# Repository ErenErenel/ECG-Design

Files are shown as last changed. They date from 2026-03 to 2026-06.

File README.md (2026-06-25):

# ECG Instrumentation & Heart Rate Variability Analysis

An analog ECG front-end (instrumentation amplifier + filtering) built around the
**OP484** quad op-amp, together with a Python analysis of the acquired signal for
beat-by-beat heart rate and heart rate variability (HRV).

Developed for the **EE 495 ECG Lab** at Northwestern University.

## Analog Front-End

A Lead-I ECG is acquired with RA and LA as the differential inputs and RL as the
right-leg reference ground. The signal chain runs on a single OP484 (four op-amps,
±5 V supply):

- **Instrumentation amplifier (3 op-amps)** — total gain ≈ 25
  - First stage (differential): G₁ = (2R₂ + R₁)/R₁ = 5, with R₂ = 20 kΩ, R₁ = 10 kΩ
  - Second stage (difference amp): G₂ = R₆/R₄ = 5, with R₆ = 100 kΩ, R₄ = 20 kΩ
- **Gain + filtering stage (4th op-amp)** — additional gain and approximate
  1–100 Hz band-limiting (high-pass + low-pass) to suppress baseline drift and
  high-frequency interference.

Bench verification with a 10 mV differential sine drove an output near 0.25 V,
confirming the ×25 instrumentation-amp gain across the 1–1000 Hz range.

## Heart Rate & HRV Analysis

A ~1-minute Lead-I recording was digitized at **fₛ = 1000 Hz** and analyzed in Python:

- **R-peak detection** — threshold-based (750 mV) with a 0.25 s refractory period and
  recovery of missed beats from abnormally long RR intervals. **72 R-peaks** detected.
- **Beat-by-beat heart rate** — computed from RR intervals (HRᵢ = 60 / RRᵢ),
  starting around 74.6 bpm.
- **HRV spectral analysis** — the mean HR is removed and an FFT-based power spectrum
  of the HR signal shows most variability at low frequencies (≤ 2 Hz, with a bump near
  ~0.18 Hz) associated with autonomic / respiratory modulation.

## Repository Structure

```
ECG-Design/
├── ECG PCB Files/          KiCad schematic, layout, and project for the ECG board
│   ├── ECG.kicad_sch
│   ├── ECG.kicad_pcb
│   └── ECG.kicad_pro
├── EE495 ECG Lab.pdf       Lab report: instrumentation amp design + ECG acquisition
└── Heart Rate Variability Analysis.pdf
                            HR and HRV analysis of the recorded ECG
```

Open `ECG PCB Files/ECG.kicad_pro` in **KiCad 7+** to view the schematic and board.

## License

Released under the [MIT License](LICENSE).

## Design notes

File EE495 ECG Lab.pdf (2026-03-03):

# EE495 ECG Lab Project

## Part 1: Instrumentation Amplifier

The instrumentation amplifier (Figure 1) was implemented using three OP484 op-amps powered by ±5 V.

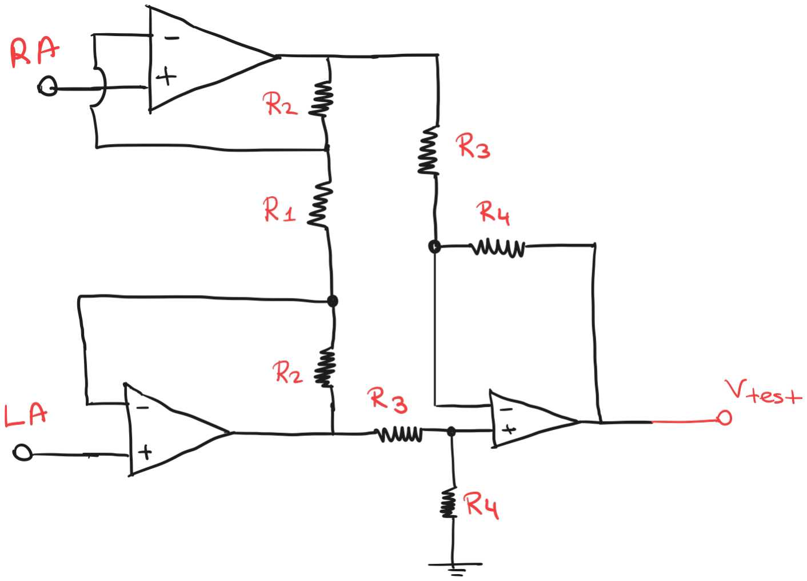
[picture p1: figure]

Figure 1: Instrumentation amplifier schematic

First stage (differential) gain G! = 2R" + R!
R!

with R" = 20 kΩ, R! = 10 kΩ:
G! = 2(20k) + 10k

10k = 50k 10k = 5

Second stage (difference amplifier) gain G" = R#
R$

with R# = 100 kΩ, R$ = 20 kΩ:
G" = 100k
20k = 5
Total instrumentation amplifier gain GINA = G!G" = 5 × 5 = 25

Bench verification: The amplifier was driven using a 10 mV differential sine wave generated by the Analog Discovery through a resistor attenuator. The measured output amplitude at Vtest was approximately 0.25 V, confirming a gain near 25 across the 1–1000 Hz test range.

ECG acquisition: A Lead-I ECG was acquired with RA and LA as the differential inputs and RL as the reference (right-leg ground). The resulting waveform (Plot 1) shows ECG morphology with noticeable high-frequency interference and baseline drift typical of unfiltered acquisition.

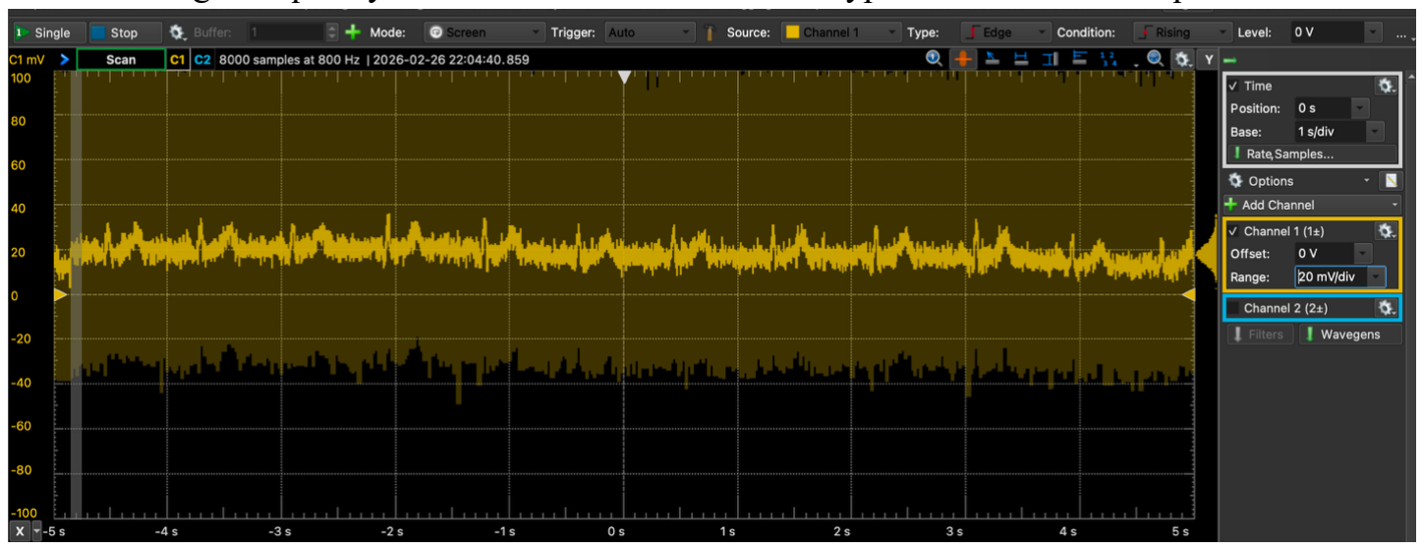
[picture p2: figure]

Plot 1: Lead-I ECG after instrumentation amplifier (G ≈ 25)

## Part 2: Additional Amplification + Filtering

The fourth OP484 op-amp was used to add additional gain and implement approximate 1–100 Hz band-limiting (Figure 2).

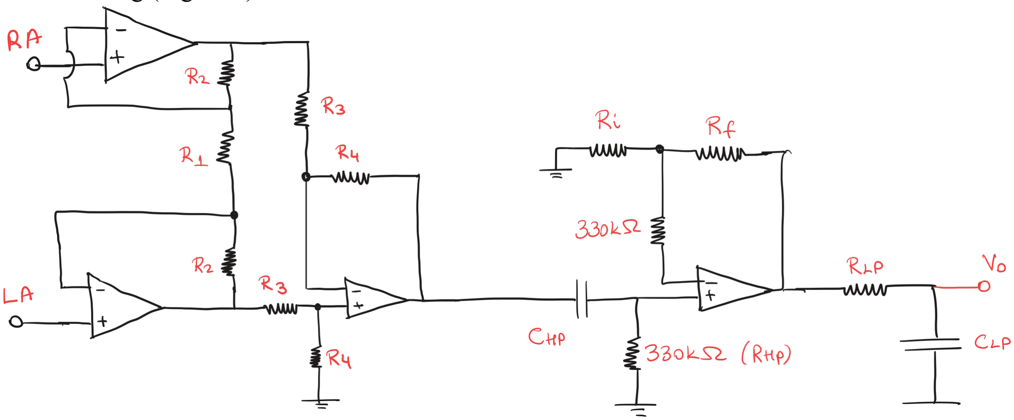
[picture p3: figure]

Figure 2: Full ECG amplifier circuit (INA + filter/gain stage)

High-pass filter
f%& = 1 2πR%&C%&

with R%& = 330 kΩ, C%& = 0.47 μF:
f%& = | 1
2π(330k)(0.47μ) ≈ 1.03 Hz

This attenuates electrode DC offset and low-frequency baseline drift.

Second-stage non-inverting gain

Gstage2 = 1 +

R'
R⁽

with R' = 330 kΩ, R⁽ = 33 kΩ:

Gstage2 = 1 +

330k
33k = 11

Low-pass filter (noise reduction) f)& = 1
2πR)&C)&

with R)& = 33 kΩ, C)& = 0.047 μF:
f)& = | 1
2π(33k)(0.047μ) ≈ 103 Hz

This significantly reduces high-frequency noise while preserving QRS morphology.

Overall gain
Gtotal = GINA ⋅ Gstage2 = 25 × 11 = 275

## ECG acquisition

Lead-I ECG was recorded again using the complete amplifier. Compared to Part 1, the final output (Plot 2) shows substantially reduced high-frequency interference and improved readability of ECG features.

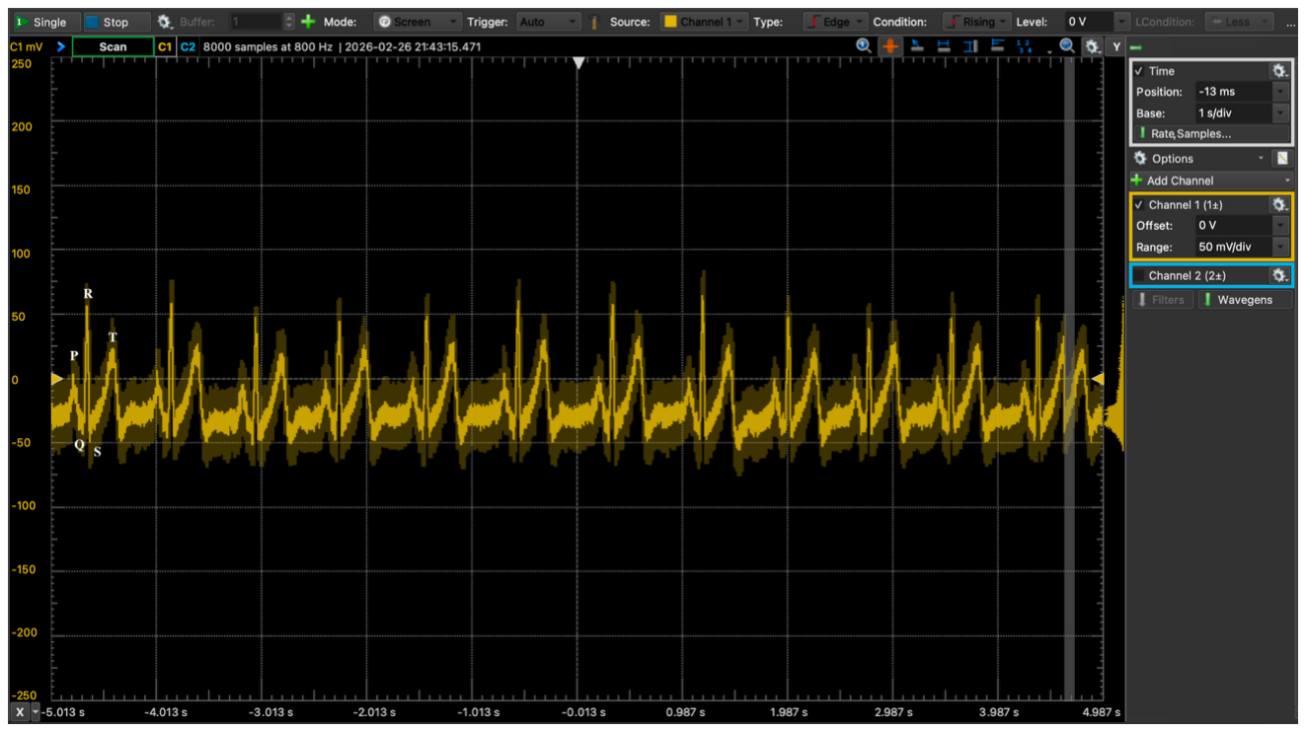
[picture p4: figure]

Plot 2: Lead-I ECG after full amplifier (G ≈ 275, ~1–100 Hz)

## Digitization and Digital Post-Processing (1-minute recording)

A continuous 1-minute Lead-I ECG recording was stored using the Analog Discovery in 16-bit signed binary format at a 1024 Hz sampling rate for analysis in Python. For visualization, a digital 60 Hz notch filter was applied to further suppress power-line interference.

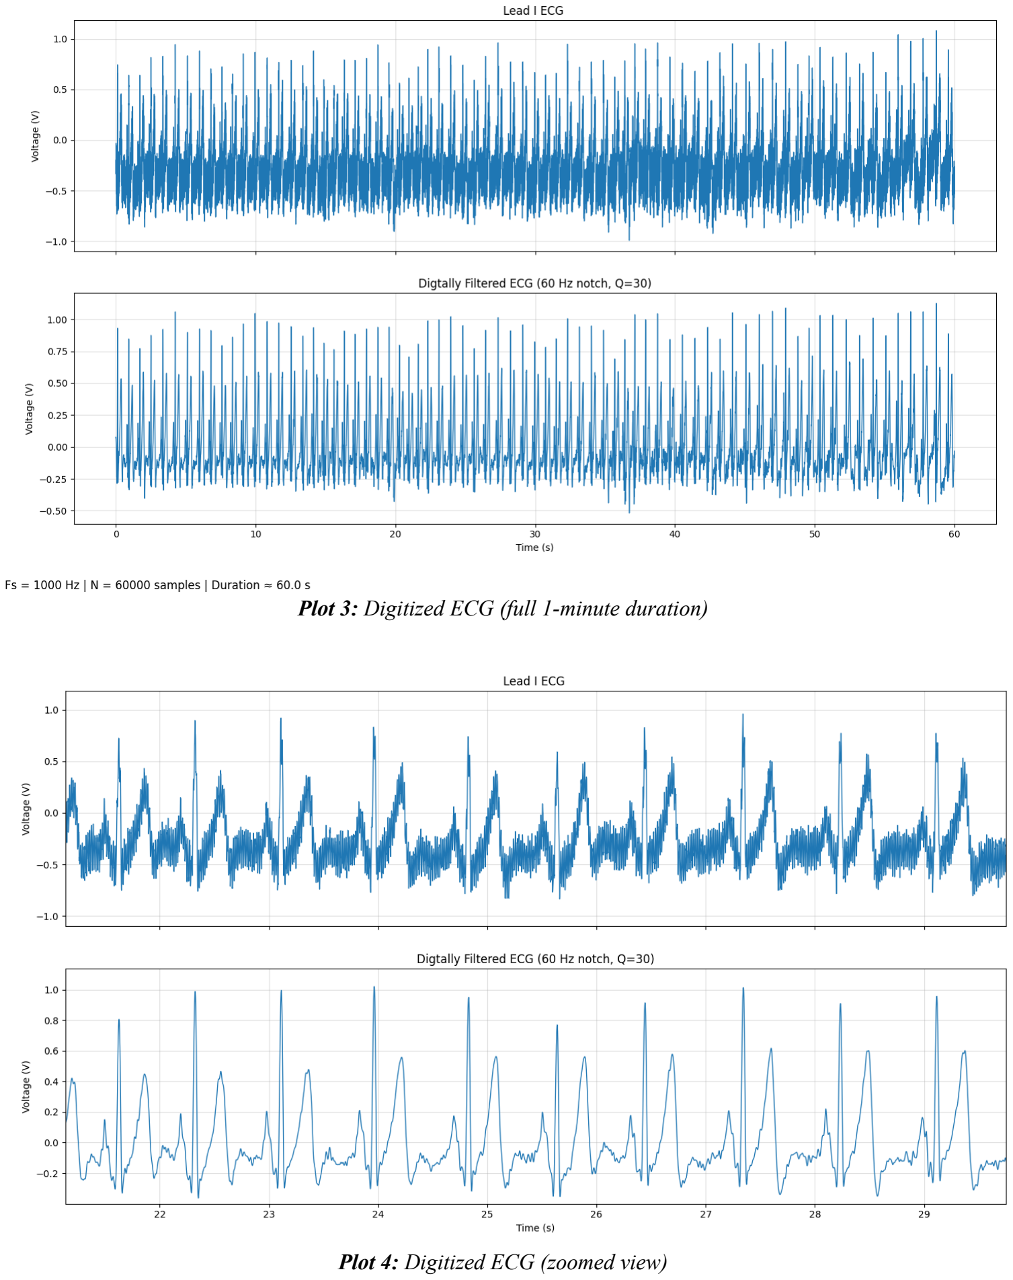
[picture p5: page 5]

Plot 3: Digitized ECG (full 1-minute duration)

Plot 4: Digitized ECG (zoomed view)

In the zoomed view (Plot 4), removing 60 Hz interference improves visibility of lower-amplitude features; in particular, a small post–T-wave deflection that could indicate a U wave is more clearly resolved rather than being masked by high-frequency noise.

Appendix:
import numpy as np
import matplotlib.pyplot as plt
from scipy.signal import filtfilt, iirnotch

# User settings

fs = 1000.0
path = "/Users/erenerenel/Desktop/EE495/EE495 Code/default.csv"

NOTCH_HZ = 60.0
NOTCH_Q = 30.0

# Load CSV

data = np.genfromtxt(path, delimiter=",", comments="#", invalid_raise=False) data = np.atleast_2d(data)
data = data[~np.all(np.isnan(data), axis=1)]

print("Loaded shape:", data.shape)
if data.shape[0] < 1000:
raise ValueError("CSV loaded too few rows")

col0 = data[:, 0]
is_time_like = np.all(np.diff(col0[:200]) > 0) and (np.nanmedian(np.diff(col0[:200])) < 0.05)

if data.shape[1] >= 2 and is_time_like:
t = col0
c1_volts = data[:, 1]
else:
c1_volts = data[:, 0]
t = np.arange(c1_volts.size) / fs

mask = ~np.isnan(c1_volts)
c1_volts = c1_volts[mask]
t = t[mask]

print("Samples:", c1_volts.size, "Duration(s):", (t[-1] - t[0]) if t.size else 0)

# Filtering

bN, aN = iirnotch(NOTCH_HZ, Q=NOTCH_Q, fs=fs)
ecg_filt = filtfilt(bN, aN, c1_volts)

# Plot

raw_mv = c1_volts / 1000
filt_mv = ecg_filt / 1000

fig, ax = plt.subplots(2, 1, sharex=True, figsize=(10, 6))

ax[0].plot(t, raw_mv, linewidth=1.0) ax[0].set_title("Lead I ECG ")
ax[0].set_ylabel("Voltage (V)") ax[0].grid(True, alpha=0.4)

ax[1].plot(t, filt_mv, linewidth=1.0)
ax[1].set_title(
f"Digtally Filtered ECG ({NOTCH_HZ:g} Hz notch, Q={NOTCH_Q:g})" )
ax[1].set_xlabel("Time (s)")
ax[1].set_ylabel("Voltage (V)")
ax[1].grid(True, alpha=0.4)

duration_s = t[-1] - t[0]
fig.text(
0.01, 0.01,
f"Fs = {fs:g} Hz | N = {len(t)} samples | Duration ≈ {duration_s:.1f} s",
fontsize=12
)

fig.tight_layout(rect=[0, 0.02, 1, 1]) plt.show()

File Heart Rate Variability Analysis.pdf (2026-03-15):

## Beat-by-Beat Heart Rate and Heart Rate Variability Analysis

## Introduction

An ECG signal recorded using the ECG instrumentation amplifier built during the laboratory exercise was analyzed to compute beat-by-beat heart rate (HR) and heart rate variability (HRV). The ECG was recorded in a Lead-I configuration with right-leg grounding for approximately one minute and digitized at a sampling rate of:
fs = 1000 Hz

All analysis was implemented in Python.

## 1. Beat-by-Beat Heart Rate Measurement

R-Peak Detection
R-peaks were detected from the ECG using a threshold-based algorithm:
1. A voltage threshold of 750 mV was used to identify candidate QRS complexes.
2. The local maximum within each threshold crossing was selected as the R-peak.
3. A refractory period of 0.25 s prevented multiple detections within the same QRS complex.
4. Missed beats were recovered by identifying abnormally large RR intervals and searching for the largest peak within that interval (as some of the R-peaks were below the set 750 mV).
A total of 72 R-peaks were detected in the one-minute ECG recording.

ECG with Detected Peaks

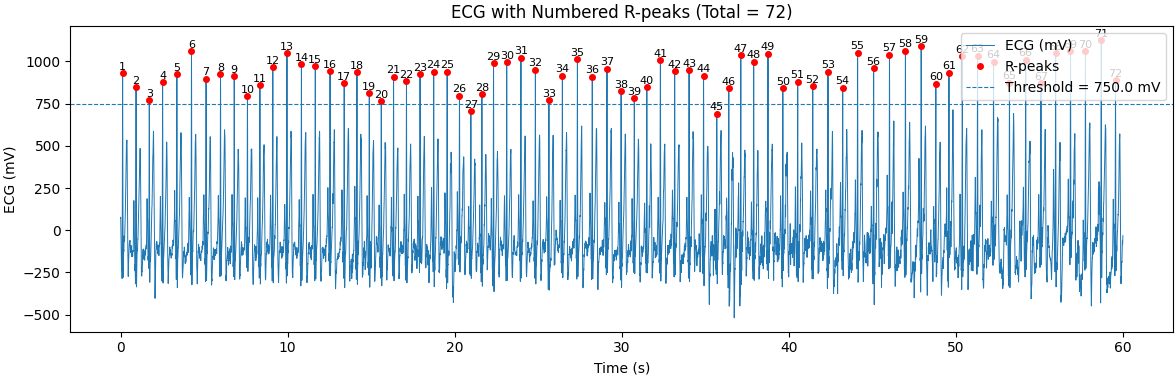
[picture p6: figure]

Figure 1: ECG recording used in the analysis with detected R-peaks labeled.

To improve visualization, the ECG was also segmented into groups of 24 beats.

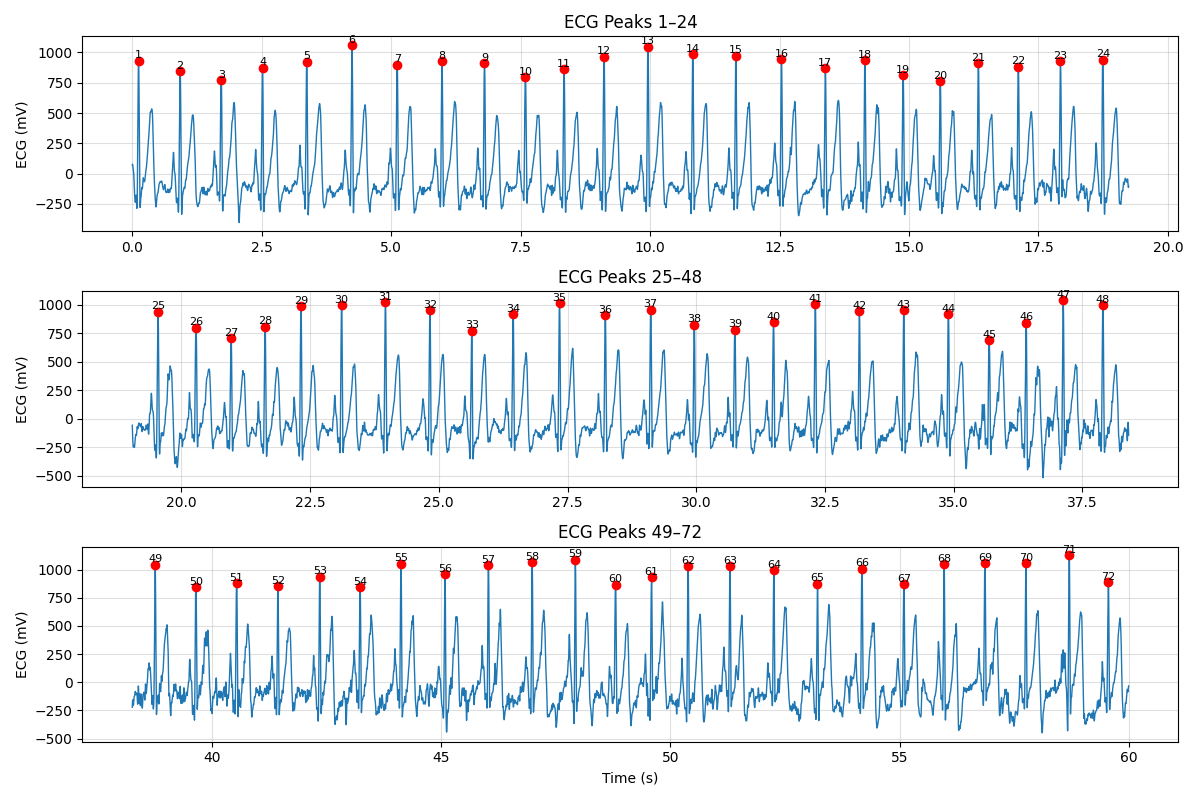
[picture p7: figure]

Figure 2: Segmented ECG plots showing detected peaks.

Beat-by-Beat Heart Rate
Heart rate was calculated from the RR intervals between consecutive R-peaks: RRi = ti − ti−1

HRi =

60
RRi

where RRi

is the interval between beats in seconds and HRi is the instantaneous heart rate in beats per minute (bpm).
The resulting values provide a beat-by-beat estimate of heart rate over the one-minute recording (Values in Appendix.A)

## 2. Heart Rate Variability

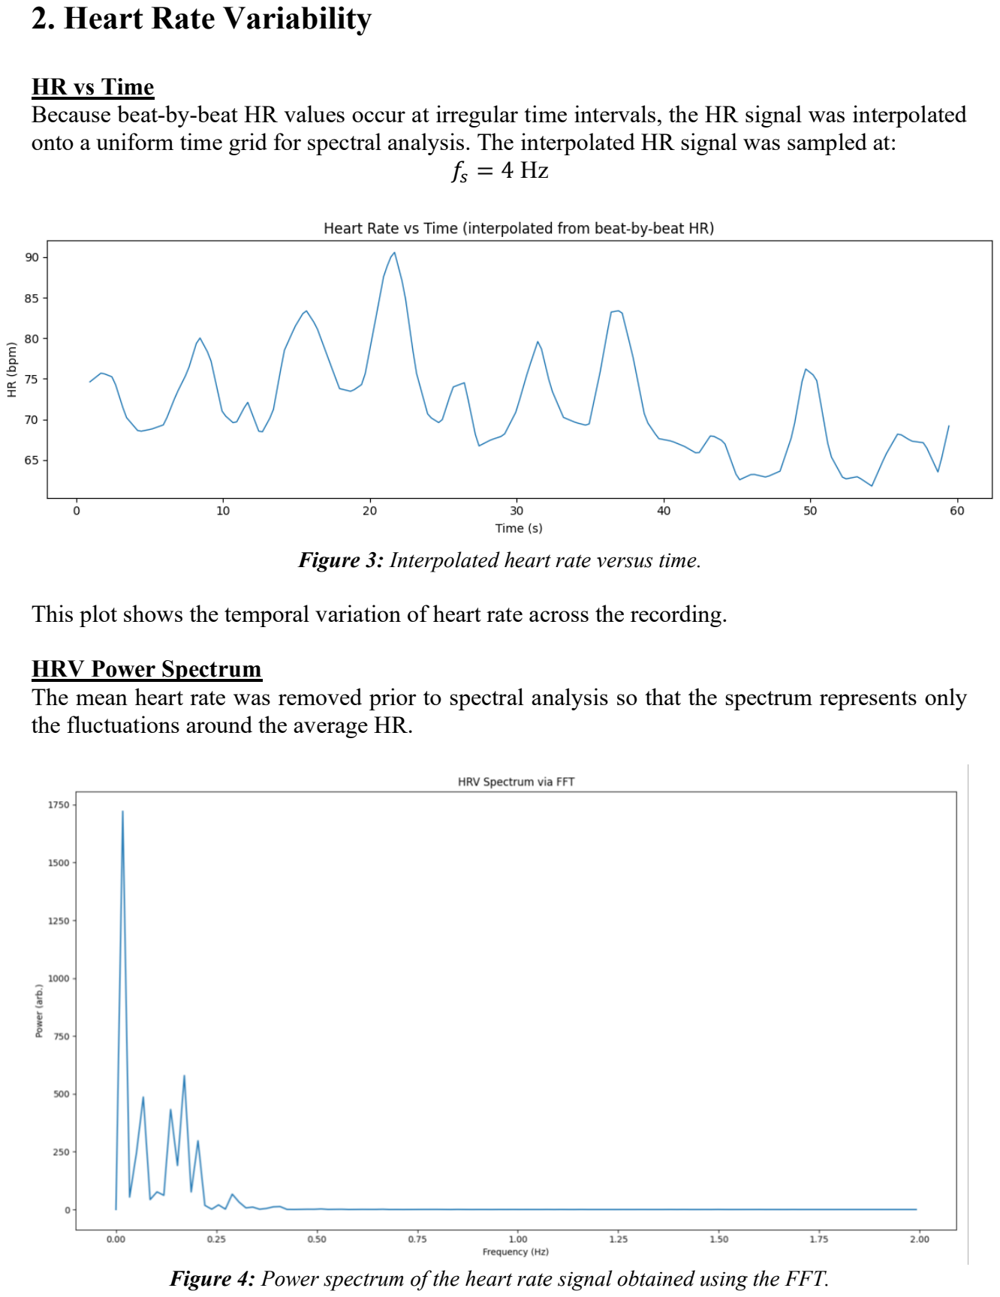
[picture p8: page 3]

HR vs Time
Because beat-by-beat HR values occur at irregular time intervals, the HR signal was interpolated onto a uniform time grid for spectral analysis. The interpolated HR signal was sampled at:
fs = 4 Hz

Figure 3: Interpolated heart rate versus time.

This plot shows the temporal variation of heart rate across the recording.

HRV Power Spectrum
The mean heart rate was removed prior to spectral analysis so that the spectrum represents only the fluctuations around the average HR.

Figure 4: Power spectrum of the heart rate signal obtained using the FFT.

The HRV spectrum shows that most variability occurs at low frequencies (≤ 2 Hz , especially the bump at ~ 0.18 Hz). These slow fluctuations are associated with the autonomic regulation of heart rate and indicative of the respiratory rate. Higher frequency components contain comparatively less power.

# Conclusion

Beat-by-beat heart rate and heart rate variability were successfully computed from a one-minute ECG recording. R-peaks were detected using a threshold-based method with refractory filtering and missed-beat recovery.
Heart rate was calculated from RR intervals and interpolated to form a uniformly sampled HR signal.
Spectral analysis of this signal revealed that HR variability is primarily concentrated at frequencies around 0.15 – 0.20 Hz.

*Code used in the report can be found in Appendix.B.

## Appendix

Appendix.A
Beat-by-beat HR list (bpm):
001: t = 0.925 s HR = 74.63 bpm 002: t = 1.717 s HR = 75.76 bpm 003: t = 2.515 s HR = 75.19 bpm 004: t = 3.368 s HR = 70.34 bpm 005: t = 4.244 s HR = 68.49 bpm 006: t = 5.116 s HR = 68.81 bpm 007: t = 5.981 s HR = 69.36 bpm 008: t = 6.802 s HR = 73.08 bpm 009: t = 7.592 s HR = 75.95 bpm 010: t = 8.339 s HR = 80.32 bpm 011: t = 9.111 s HR = 77.72 bpm 012: t = 9.959 s HR = 70.75 bpm 013: t = 10.824 s HR = 69.36 bpm 014: t = 11.655 s HR = 72.20 bpm 015: t = 12.537 s HR = 68.03 bpm 016: t = 13.384 s HR = 70.84 bpm 017: t = 14.149 s HR = 78.43 bpm 018: t = 14.886 s HR = 81.41 bpm 019: t = 15.604 s HR = 83.57 bpm 020: t = 16.340 s HR = 81.52 bpm 021: t = 17.112 s HR = 77.72 bpm 022: t = 17.925 s HR = 73.80 bpm 023: t = 18.742 s HR = 73.44 bpm 024: t = 19.548 s HR = 74.44 bpm 025: t = 20.285 s HR = 81.41 bpm 026: t = 20.967 s HR = 87.98 bpm 027: t = 21.627 s HR = 90.91 bpm 028: t = 22.324 s HR = 86.08 bpm 029: t = 23.113 s HR = 76.05 bpm 030: t = 23.965 s HR = 70.42 bpm 031: t = 24.829 s HR = 69.44 bpm 032: t = 25.640 s HR = 73.98 bpm 033: t = 26.445 s HR = 74.53 bpm 034: t = 27.345 s HR = 66.67 bpm

035: t = 28.234 s HR = 67.49 bpm 036: t = 29.116 s HR = 68.03 bpm 037: t = 29.961 s HR = 71.01 bpm 038: t = 30.751 s HR = 75.95 bpm 039: t = 31.501 s HR = 80.00 bpm 040: t = 32.313 s HR = 73.89 bpm 041: t = 33.167 s HR = 70.26 bpm 042: t = 34.029 s HR = 69.61 bpm 043: t = 34.896 s HR = 69.20 bpm 044: t = 35.686 s HR = 75.95 bpm 045: t = 36.407 s HR = 83.22 bpm 046: t = 37.126 s HR = 83.45 bpm 047: t = 37.897 s HR = 77.82 bpm 048: t = 38.754 s HR = 70.01 bpm 049: t = 39.641 s HR = 67.64 bpm 050: t = 40.532 s HR = 67.34 bpm 051: t = 41.432 s HR = 66.67 bpm 052: t = 42.345 s HR = 65.72 bpm 053: t = 43.226 s HR = 68.10 bpm 054: t = 44.118 s HR = 67.26 bpm 055: t = 45.078 s HR = 62.50 bpm 056: t = 46.026 s HR = 63.29 bpm 057: t = 46.980 s HR = 62.89 bpm 058: t = 47.923 s HR = 63.63 bpm 059: t = 48.801 s HR = 68.34 bpm 060: t = 49.587 s HR = 76.34 bpm 061: t = 50.385 s HR = 75.19 bpm 062: t = 51.297 s HR = 65.79 bpm 063: t = 52.255 s HR = 62.63 bpm 064: t = 53.208 s HR = 62.96 bpm 065: t = 54.179 s HR = 61.79 bpm 066: t = 55.094 s HR = 65.57 bpm 067: t = 55.972 s HR = 68.34 bpm 068: t = 56.863 s HR = 67.34 bpm 069: t = 57.757 s HR = 67.11 bpm 070: t = 58.703 s HR = 63.42 bpm 071: t = 59.557 s HR = 70.26 bpm

Appendix.B
import numpy as np
import matplotlib.pyplot as plt

# =========================

# USER SETTINGS

# =========================

fs_ecg = 1000.0 | # ECG sampling rate (Hz)
thr_mV = 750.0 | # initial threshold for R-peak detection (mV)
refractory_s = 0.25 | # minimum time between detected peaks (s)

# RR-gap recovery (missed-beat insertion)

gap_factor = 1.4 # if RR > gap_factor * median_RR, search for a missed peak search_margin_s = 0.12 # ignore +/- margin around interval edges when searching (s) max_insert_passes = 5 # safety cap

# HR(t) resampling for HRV

fs_hr = 4.0 | # Hz uniform grid for HR-vs-time

# Input file: ECG in mV

path = "/Users/erenerenel/Desktop/EE495/EE495 Code/ecg_final_filtered.csv"

# =========================

# LOAD CSV

# =========================

data = np.genfromtxt(path, delimiter=",", comments="#", invalid_raise=False) data = np.asarray(data)

if data.ndim == 0:
raise ValueError("CSV load failed (got scalar). Check file path / contents.")

if data.ndim == 1:
y_mV = data.astype(float)
t = np.arange(y_mV.size) / fs_ecg else:

# drop rows that are all-NaN

data = data[~np.all(np.isnan(data), axis=1)]

# one long row -> flatten

if data.shape[0] == 1 and data.shape[1] > 1: y_mV = data.ravel().astype(float)
t = np.arange(y_mV.size) / fs_ecg
else:
col0 = data[:, 0]
ncheck = min(200, len(col0)) is_time_like = (
ncheck >= 10
and np.all(np.diff(col0[:ncheck]) > 0)
and (np.nanmedian(np.diff(col0[:ncheck])) < 0.01) )
if data.shape[1] >= 2 and is_time_like:
t = col0.astype(float)
y_mV = data[:, 1].astype(float) else:
y_mV = data[:, 0].astype(float)
t = np.arange(y_mV.size) / fs_ecg

mask = ~np.isnan(y_mV) & ~np.isnan(t) y_mV = y_mV[mask]
t = t[mask]

if y_mV.size < 1000:
raise ValueError(f"Too few samples loaded: {y_mV.size}")

duration_s = t[-1] - t[0]
print(f"Loaded samples: {y_mV.size}, duration ≈ {duration_s:.2f} s")

# =========================

# INITIAL R-PEAK DETECTION:

# threshold -> contiguous segments -> local max per segment -> refractory # =========================

above = y_mV > thr_mV
edges = np.diff(above.astype(int))

starts = np.where(edges == 1)[0] + 1 ends = np.where(edges == -1)[0] + 1

if above[0]:
starts = np.r_[0, starts]
if above[-1]:
ends = np.r_[ends, y_mV.size]

if starts.size == 0 or ends.size == 0:
raise ValueError("No above-threshold segments found. Lower thr_mV or check units.")

# candidate peak: local max in each above-threshold segment

cand_idx = []
for s, e in zip(starts, ends):
if e <= s:
continue
idx = s + int(np.argmax(y_mV[s:e])) cand_idx.append(idx)
cand_idx = np.array(cand_idx, dtype=int)

# refractory filter

keep = []
last_t = -np.inf
for idx in cand_idx:
if (t[idx] - last_t) >= refractory_s: keep.append(idx)
last_t = t[idx]
r_idx = np.array(keep, dtype=int)

# sort / unique just in case r_idx = np.unique(r_idx)

r_idx = r_idx[np.argsort(t[r_idx])]

print(f"Initial detected beats: {len(r_idx)}")

# =========================

# MISSED-BEAT RECOVERY:

# If RR gap is too long (> gap_factor * median RR),

# search between peaks for the largest local maximum and insert it. # Repeat a few passes in case multiple misses exist.

# =========================

margin = int(search_margin_s * fs_ecg)

for _pass in range(max_insert_passes): r_t = t[r_idx]
if r_t.size < 3:
break

rr = np.diff(r_t)
med_rr = np.median(rr)

new_idxs = []
for i, rr_i in enumerate(rr):
if rr_i > gap_factor * med_rr: s = r_idx[i] + margin
e = r_idx[i + 1] - margin
if e <= s:
continue

# Find the strongest peak in the gap

idx = s + int(np.argmax(y_mV[s:e]))

# Enforce refractory vs neighboring peaks

if (t[idx] - t[r_idx[i]]) >= refractory_s and (t[r_idx[i + 1]] - t[idx]) >= refractory_s: new_idxs.append(idx)

if not new_idxs:
break r_idx = np.unique(np.concatenate([r_idx, np.array(new_idxs, dtype=int)])) r_idx = r_idx[np.argsort(t[r_idx])]

print(f"Beats after RR-gap recovery: {len(r_idx)}")

# =========================

# HR (beat-by-beat)

# =========================

r_t = t[r_idx]
r_y = y_mV[r_idx]

if r_t.size < 2:
raise ValueError("Need at least 2 peaks to compute HR. Lower thr_mV or check signal.")

rr_s = np.diff(r_t)
hr_bpm = 60.0 / rr_s
hr_t = r_t[1:]

print("\nBeat-by-beat HR list (bpm):")
for i, (ti, hri) in enumerate(zip(hr_t, hr_bpm), start=1): print(f"{i:03d}: t = {ti:7.3f} s HR = {hri:6.2f} bpm")

# =========================

# HR vs time (interpolate to uniform grid) # =========================

t0, t1 = hr_t[0], hr_t[-1]
t_hr_grid = np.arange(t0, t1, 1.0 / fs_hr) hr_grid = np.interp(t_hr_grid, hr_t, hr_bpm) hr_grid_zero = hr_grid - np.mean(hr_grid)

# =========================

# PLOTS

# 1) ECG with numbered R-peaks

# 2) Segmented ECG peak plots # 3) HR vs time

# 4) FFT^2

# =========================

# ========================= # FULL ECG PLOT WITH PEAKS # =========================

plt.figure(figsize=(12, 4))
plt.plot(t, y_mV, linewidth=0.7, label="ECG (mV)")
plt.plot(r_t, r_y, "ro", markersize=4, label="R-peaks")
plt.axhline(thr_mV, linestyle="--", linewidth=0.8, label=f"Threshold = {thr_mV} mV") for i, (ti, yi) in enumerate(zip(r_t, r_y), start=1):
plt.text(ti, yi + 20, str(i), fontsize=8, ha="center")
plt.title(f"ECG with Numbered R-peaks (Total = {len(r_t)})")
plt.xlabel("Time (s)")
plt.ylabel("ECG (mV)")
plt.legend(loc="upper right")
plt.tight_layout()
plt.show()

# ========================= # SEGMENTED ECG PEAK PLOTS # ========================= peaks_per_plot = 24

num_peaks = len(r_t)
num_plots = int(np.ceil(num_peaks / peaks_per_plot))

fig, axes = plt.subplots(num_plots, 1, figsize=(12, 8), sharex=False)

if num_plots == 1:
axes = [axes]

for p in range(num_plots):

start_peak = p * peaks_per_plot
end_peak = min((p + 1) * peaks_per_plot, num_peaks)

# time window from first peak to last peak in this segment t_start = r_t[start_peak] - 0.5

t_end = r_t[end_peak - 1] + 0.5

mask = (t >= t_start) & (t <= t_end)

axes[p].plot(t[mask], y_mV[mask], linewidth=1.0)

# plot peaks in this segment

seg_peaks = r_idx[start_peak:end_peak] axes[p].plot(t[seg_peaks], y_mV[seg_peaks], "ro")

# number peaks

for i, idx in enumerate(seg_peaks, start=start_peak + 1): axes[p].text(t[idx], y_mV[idx] + 20, str(i), fontsize=8, ha='center')

axes[p].set_title(f"ECG Peaks {start_peak+1}–{end_peak}") axes[p].set_ylabel("ECG (mV)")
axes[p].grid(True, alpha=0.4)

axes[-1].set_xlabel("Time (s)")

plt.tight_layout()
plt.show()

# ========================= # HR vs time (Interpolated)

# =========================

plt.figure(figsize=(12, 4))
plt.plot(t_hr_grid, hr_grid, linewidth=1.0)
plt.title("Heart Rate vs Time (interpolated from beat-by-beat HR)") plt.xlabel("Time (s)")

plt.ylabel("HR (bpm)")
plt.tight_layout()
plt.show()

# ========================= # FFT OF HR SIGNAL

# =========================

N = len(hr_grid_zero)
freq_fft = np.fft.rfftfreq(N, d=1/fs_hr)

fft_vals = np.fft.rfft(hr_grid_zero) fft_mag = np.abs(fft_vals)**2 / N

print(np.mean(hr_grid_zero)) print(fft_vals[0])
dc_power = fft_mag[0]
print(f"Power at 0 Hz = {dc_power:.6e}")

plt.figure(figsize=(12,4))
plt.plot(freq_fft, fft_mag)

plt.title("HRV Spectrum via FFT") plt.xlabel("Frequency (Hz)") plt.ylabel("Power (arb.)")

plt.tight_layout()
plt.show()

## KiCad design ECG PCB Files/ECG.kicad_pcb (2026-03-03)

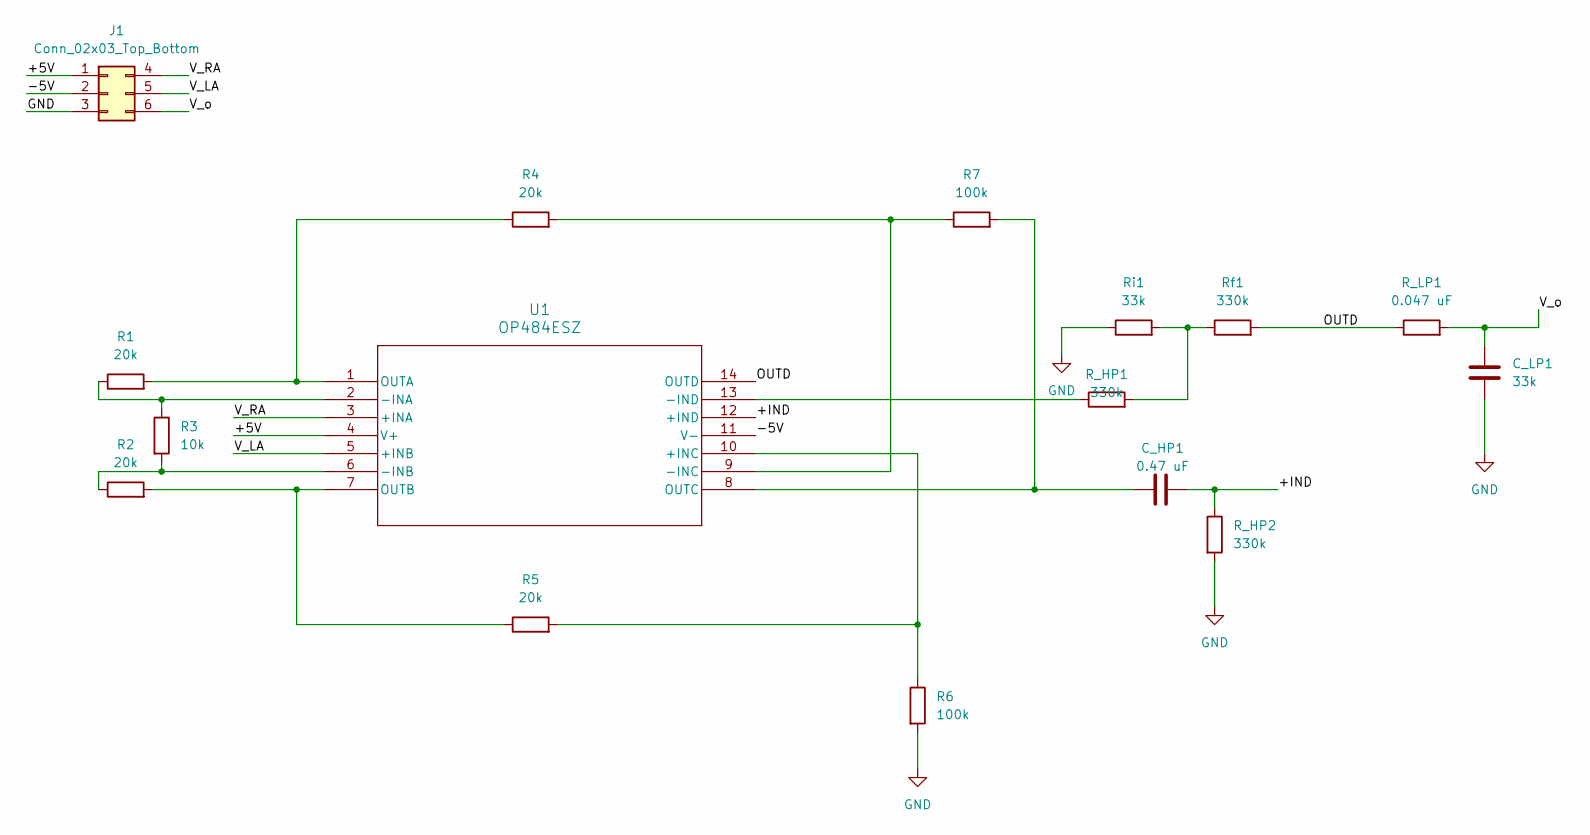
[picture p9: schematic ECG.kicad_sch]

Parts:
C_HP1: 0.47 uF; C_0805_2012Metric
C_LP1: 33k; C_0805_2012Metric
J1: Conn_02x03_Top_Bottom; PinHeader_2x03_P2.54mm_Vertical
R1, R2, R4, R5: 20k; R_0805_2012Metric
R3: 10k; R_0805_2012Metric
R6, R7: 100k; R_0805_2012Metric
R_HP1, R_HP2: 330k; R_0805_2012Metric
R_LP1: 0.047 uF; R_0805_2012Metric
Rf1: 330k; R_0805_2012Metric
Ri1: 33k; R_0805_2012Metric
U1: OP484ESZ; R_14_ADI

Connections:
/+5V: J1.1, U1.4 (V+)
/+IND: C_HP1.2, R_HP2.1, U1.12 (+IND)
/-5V: J1.2, U1.11 (V-)
/OUTD: R_LP1.1, Rf1.2, U1.14 (OUTD)
/V_LA: J1.5, U1.5 (+INB)
/V_RA: J1.4, U1.3 (+INA)
/V_o: C_LP1.1, J1.6, R_LP1.2
GND: C_LP1.2, J1.3, R6.2, R_HP2.2, Ri1.1
unnamed: R_HP1.2, Rf1.1, Ri1.2
unnamed: R5.2, R6.1, U1.10 (+INC)
unnamed: R1.1, R3.1, U1.2 (-INA)
unnamed: R2.1, R3.2, U1.6 (-INB)
unnamed: R4.2, R7.1, U1.9 (-INC)
unnamed: R_HP1.1, U1.13 (-IND)
unnamed: R1.2, R4.1, U1.1 (OUTA)
unnamed: R2.2, R5.1, U1.7 (OUTB)
unnamed: C_HP1.1, R7.2, U1.8 (OUTC)

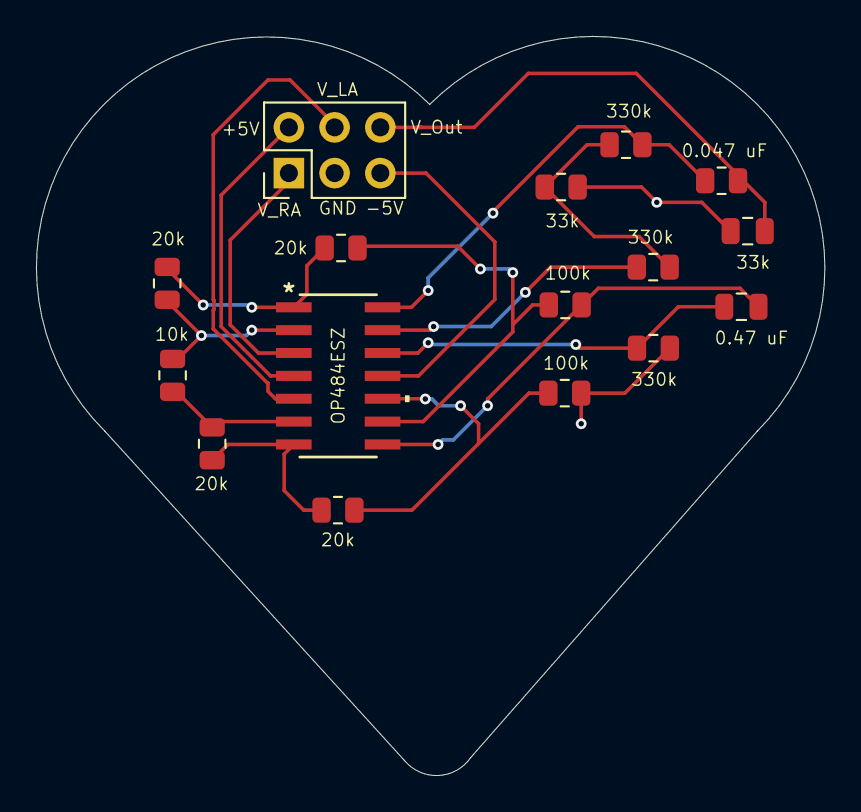
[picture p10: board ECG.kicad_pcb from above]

Board: 2 copper layers, 43.8 x 41.1 mm, 16 parts (0 on the bottom side), 17 nets.
